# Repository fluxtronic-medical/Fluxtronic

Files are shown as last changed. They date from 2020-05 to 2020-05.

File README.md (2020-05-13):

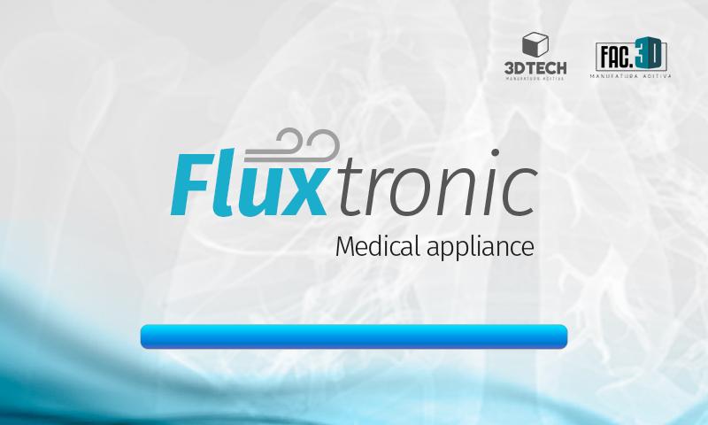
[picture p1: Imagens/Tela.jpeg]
 
 
# FLUXTRONIC
 
## ⚠️  ATENÇÃO! ANTES DE COMPARTILHAR OU REALIZAR DOWNLOADS, ESTEJA CIENTE DOS SEGUINTES ITENS:
 
**Este projeto ainda está em desenvolvimento. Não é um produto pronto e ainda não está apto a fabricação em escala. Ainda temos muito trabalho a ser feito, verifique o status do projeto e veja como pode colaborar.**
 
 **[IN PROGRESS]****[IN PROGRESS]****[IN PROGRESS]****[IN PROGRESS]****[IN PROGRESS]**
-----------------------------------------------------------------------------------------------------------------

#### Video de funcionamento do equipamento

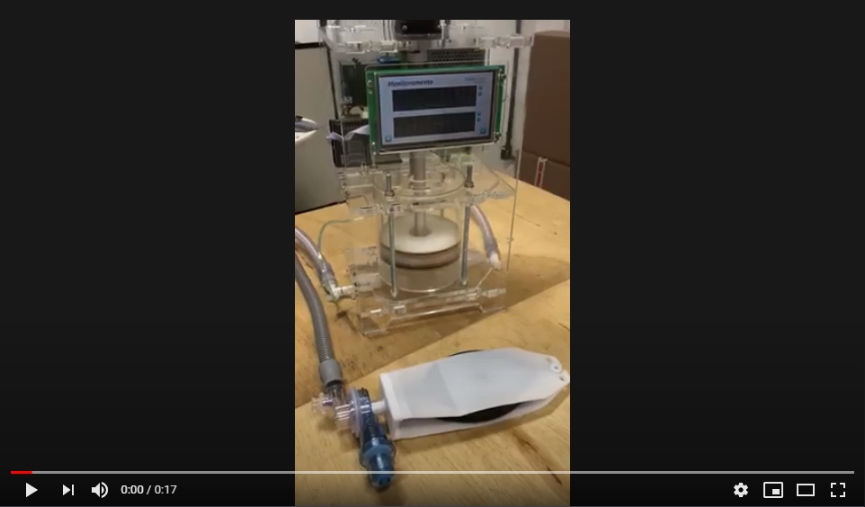
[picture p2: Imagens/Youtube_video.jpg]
Watch the video (https://www.youtube.com/watch?v=dyl--hyxr6U&feature=youtu.be)


## Porque mais um projeto?
 
Criamos outra vertente de projeto, diferente dos que já estão em desenvolvimento, pensando principalmente nas matérias primas e itens disponíveis para fabricação dentro do Brasil que são de fácil acesso. Acreditamos que esse conceito **depois de validado** possa ser replicado com o menor tempo de fabricação e com menor custo comparado a outros projetos. 

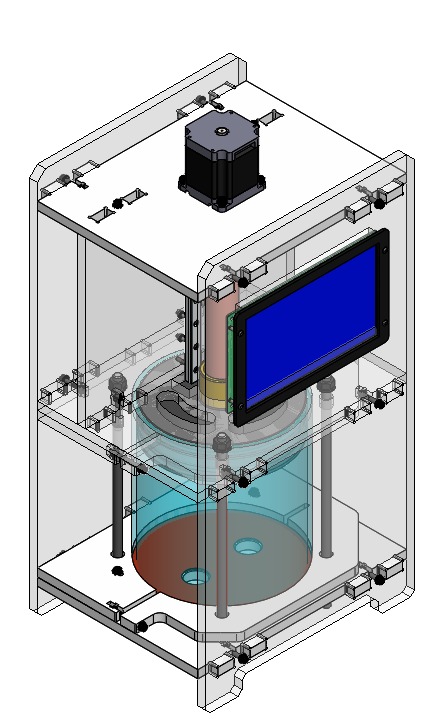
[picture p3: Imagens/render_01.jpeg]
  
# Status
 
- March 20-24: Testes mecânicos 
- March 24: Adaptação para NEMA 23 e ajustes para maior rigidez da estrutura.
- March 25: Testes de fluxo com NEMA 23 e programação do CLP.
- March 26: Programação do sistema de telemetria e controle de informações na IHM.
- March 27: Teste intenso do sistema e fadiga do equipamento
- March 28: Instalação do sensor MPX 2010 e teste de pressão
- March 29: Programação do sistema de falhas por pressão e IHM display 128x64
- March 30: Junção dos programas e limpeza do código + ~~Aferição de fluxo e pressão com equipamento de calibração~~
- March 31: Testes de alarme junto ao sistema de sensoriamento
- April 01: Liagação das válvulas e controle via CLP
- April 02: Adicionar módulo analógico CLP e comunicar via arduino
- April 03: Configuração dos equipamentos de medição para aferir o sistema + Programação CLP entrada analógica
- April 04: Migração do firmware para plataforma ESP32 | Teste e análise de fluxo
- April 05: Implementação NEXTION para leitura do gráfico + ~~ESP32~~
- April 06: Merge código de telemetria + IHM + CLP | Upload de fotos da montagem/dispositivos
- April 07: Configuração da interface IHM
- April 08: Resolução de Bug's no firmware do arduino
- April 09: Ligação do equipamento de medição (Fluxo+pressão)
- April 10: Debug IHM/arduino (comunicação serial)
- April 11: Debug IHM/arduino (comunicação serial) + adaptação válvula Peep
- April 12: Testes de sensoriamento e alarme + Mapeamento das variáveis
- April 13: Calibração da curva de respiração 
- April 14: Vídeo explicativo do sistema + avaliação Dr. Glauco Westphal

**ALTERAÇÃO DO SISTEMA MECÂNICO E ABANDONO DO ACIONAMENTO DE AMBU**

- April 15: 
- April 16:
- April 17:
- April 18:
- April 19:
- April 20:
- April 21:
- April 22:
- April 23:
- April 24:
- April 25:
- April 26:
- April 27:
- April 28:
- April 29:

### 👉 Em progresso:
 
- [x] Iniciar testes de controle de ciclo via potenciômetro
- [x] Alteração de design para junção da fixação de guia
- [x] Validação do motor NEMA 23
- [x] Validar utilização de fuso de avanço rápido 6,35x25,4 (diâmetro x passo)
- [x] Escolha do driver de motor de passo com foco em baixo custo e fácil acesso (Dimensionado p/ NEMA23)
- [x] Programação arduino para controle de ciclo e fluxo via potenciômetro
- [x] Criação da interface (espaço para 2 potenciômetros e possível tela para sensor de fluxo)
- [x] Levantamento de sensorização do sistema (qual sensor utilizar?)
- [x] Realizar testes intensivos para identificar pontos críticos nas partes de acrílico
- [x] Teste com válvulas solenóides para parada de emergência do sistema
- [x] Criação da case eletrônica
- [x] Programação CLP para leitura analógica
- [ ] ~~Controle PID do motor via CLP~~
- [x] Adaptação controle de telemetria
- [x] Testes com sensor de pressão industrial
- [ ] ~~Adaptação do código para utilização do ESP32~~
- [x] Testar MPX5010  (*06 April - Validado*)
- [x] Desenhar ligação eletrônica (Fritzing)
- [x] Armazenar os valores nas variaveis quando retornar as configurações
- [x] Corrigir bug, que faz imprimir a tela 4 antes da tela 5 quando entra em alarme de pressão pulmonar
- [x] Imprimir o valor máximo quando rotaciona o encoder no sentido anti-horário na posição mínima
- [x] Implementar saída analogica para controle de velocidade de avanço
- [x] Implementar saída analogica para controle de velocidade de recuo
- [x] Controle da curva de respiração 
- [x] Instalar nova mecânica (Atuador enclausurado)
- [x] Reunir materiais de estudo em pasta compartilhada
- [x] ~~Desligar as válvulas de inspiração/expiração e ligar a válvula de backup quando estiver em pressão pulmonar alta~~
- [ ] Desenvolvimento do Buffer de mistura 
- [x] ~~Teste do sistema blender (2-100-6016 | Oxigel)~~

### 👉 Pendente:

- [ ] Criação, validação e fabricação de PCB para entrada dos sensores e saída do motor
- [ ] Levantamento de fornecedores e estoques no Brasil dos itens de projeto
- [ ] Plotar gráfico de volume IHM
- [ ] Calibração geral dos sensores (intervalos mínimos e máximos)
- [ ] Implementação do sensor de fluxo 
- [ ] Validação das válvulas de controle I/E
- [ ] Sensor de oxigênio (Célula de oxigênio)
- [ ] Mapeamento do sistema de filtragem
- [ ] Fluxograma de controle
- [ ] Desenvolvimento do manual de operação
- [ ] Desenvolvimento material gráfico vista explodida + apresentação
- [ ] Diagrama de funcionamento do sistema
- [ ] Teste do sensor de fluxo - [ Ventilator Inline Sensor Package ](https://hackaday.io/project/170622-visp-ventilator-inline-sensor-package)

# Requisitos principais
 
1. Be reliable. It must work continuously without failure (100% duty cycle) for blocks of 14days — 24 hours a day. If necessary, the machine may be replaced after each block of 14 days x 24 hours a day use.
 
2. Provide at least two settings for volume of air/air O2 mix delivered per cycle/breath. These settings to be 450ml +/- 10ml per breath and 350ml +/- 10ml per breath.
 
3. Provide this air/air O2 mix at a peak pressure of 350 mm H2O.
 
4. Have the capability for patient supply pipework to remain pressurised at all times to 150mm H20.
 
5. Have an adjustable rate of between 12 and 20 cycles/breaths per minute.
 
6. Deliver at least 400ml of air/air 02 mix in no more than 1.5 seconds. The ability to change the rate at which air is pushed into the patient is desirable but not essential.

## Lista de material (BOM) [IN PROGRESS]

### Mecânica: 
 
- 1x Fuso DST-LS-10X25-R-ES (160mm)
- 1X Castanha DST-JFRM-C-01-DS10X25
- 1x Acoplamento para motor de passo
- 1x Patins Mgn12
- 1x Trilho Mgn12 (180mm)

#### Corte a laser (acrílico)

|       CÓDIGO         | QUANTIDADE | Espessura |
|----------------------|------------|-----------|
|   8003.200.00.01     |     01     |   10mm    |
|   8003.200.00.02     |     01     |   10mm    |
|  8003.200.00.02-1    |     01     |   10mm    |
|   8003.200.00.03     |     01     |   10mm    |
|   8003.200.00.04     |     01     |   10mm    |
|   8003.200.00.05     |     01     |   10mm    |
|   8003.200.00.06     |     01     |   10mm    |
|   8003.200.00.07     |     01     |   10mm    |
|   8003.300.00.01     |     01     |   03mm    |

### Eletrônica: 
 
- 1x Nema 23 15kg

- 1x Arduino uno
- 1x Driver de motor de passo **(DM322E)**
- 1x CLP Panasonic FP0R-C16T
- 2X Módulos de entrada/saída (8 canais)
- 1x Módulo analógico CLP (AFP0RA42)
- ~~2x Potênciometro 1K~~
- ~~1x Display 128x64~~
- 1x Encoder KY040
- 1x Fonte 24V 5A
- 1x Sensor de pressão MPX5010dp
- 1x Sensor de fluxo HAFUHH0050L4AXT
- 1x Tela Nextion 7pol
- 1x Sensor fim de curso mecânica
- 1x Fita LED (RGB)

 ### Itens médicos:

 - 1x Adaptador para conexão válvula PEEP
 - 3x tubo traqueia
 - 1x Válvula para ambu PEEP (5-20cmH20)
 - 2x Conector "Y" 22mx15F
 - 3x Fluxômetro para oxigênio
 - 1x Filtro HMEF
 - 1x Filtro HEPA

#  Material para estudo
 
Não deixe de ler sobre o assunto e entender melhor sobre como funciona um ventilador, quais suas principais funções em relação a ventilação de pacientes com COVID-19 e também alguns editais sobre:
 
- [Rapidly manufactured ventilator system specification](https://www.gov.uk/government/publications/coronavirus-covid-19-ventilator-supply-specification/rapidly-manufactured-ventilator-system-specification)
- [Specification for ventilators to be used in UK hospitals during the coronavirus (COVID-19) outbreak](https://www.gov.uk/government/publications/specification-for-ventilators-to-be-used-in-uk-hospitals-during-the-coronavirus-covid-19-outbreak)
- [Frontier Tech 4 COVID Action: emerging market ventilation systems](https://medium.com/frontier-technology-livestreaming/frontier-tech-4-covid-action-emerging-market-ventilation-systems-9c818cb46189)
- [Positive Ending Expiratory Pressure Valve](https://grabcad.com/library/positive-ending-expiratory-pressure-valve-1)
- [ANVISA By Flavia G. R. Ibagy Pacheco](https://drive.google.com/open?id=1CEK9-QgvEUpADV46hfBZcp89tQX-wVuy)

# Créditos

* Helbert Paranhos [@HPparanhos](github.com/HPparanhos) - SC
* Fellipy Kuhne  [@kinife](https://github.com/kinife) - SC
* José Manuel Ramirez [@tere.red](http://tere.red/) - SC
* Rodrigo França Formaggi [@Rodrigoformagi](https://www.linkedin.com/in/rodrigo-fran%C3%A7a-formaggi-88b730103/) - SC
* Erick Henriques Paulo Boteon [@Erick Boteon](https://www.linkedin.com/in/erick-boteon-5601a416b/) - SC
---------------------------------------------------------------------------------------------------------------
 
   > É preciso alinhar a expectativa de todos! Estamos trabalhando duro no processo de validação e rápida modificação para um projeto 100% confiável e esperamos ao máximo que isso possa salvar muitas vidas!

# ✅ Licença

Este projeto detém uma licença para produção, fabricação e desenvolvimento. Para que não hajam problemas no decorrer do tempo, é imprescindível que as mesmas sejam respeitadas e seguidas. Para mais informações acesse: 
[GNU General Public License v3.0](https://github.com/fluxtronic-medical/Fluxtronic/blob/master/LICENSE)

*Tire todas suas dúvidas antes de replicar e/ou desenvolver este projeto*

# 💰 Apoiar financeiramente

Para avançar com rapidez precisamos da sua ajuda! Saiba como colaborar com o projeto em - [DOAR](https://www.vakinha.com.br/vaquinha/acelerar-o-desenvolvimento-do-respirador-mecanico-opensource)

# Contatos e redes sociais

* Telegram [Grupo de desenvolvimento](https://t.me/joinchat/PWSd9VVRa-Q0fzXPvgVH4g)
* Instagram [@fluxtronic](https://www.instagram.com/fluxtronic/)
* Twitter [Fluxtronic - Respirador Open Source](https://twitter.com/FluxtronicOpen)
* Site Oficial [Fluxtronic.com.br](https://fluxtronic.com.br/)
* Imprensa [Fale conosco](https://web.whatsapp.com/send?phone=5547996113022)

# Empresas que apoiam essa causa

- AMS Group
- 3D Acrilicos
- Pollux Automation
- Neoyama
- Bold acrílicos
- Unimed Joinville
- OBR Equipamentos industriais
- Igus do Brasil
- JN Ferramentaria
- Docol
- Valgri
- Nidec (Embraco)
- TEX Equipamentos Eletrônicos
- Termica Solutions
- Tere.Red
- Ocotea Filmes
- Microjunta
- SR Borrachas
- Andre Toledo

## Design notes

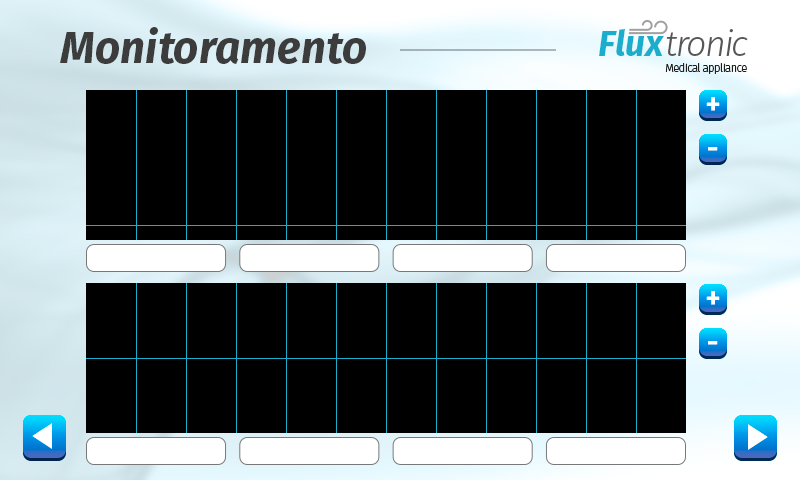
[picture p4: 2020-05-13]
IHM/Telas.png/Graficos.png

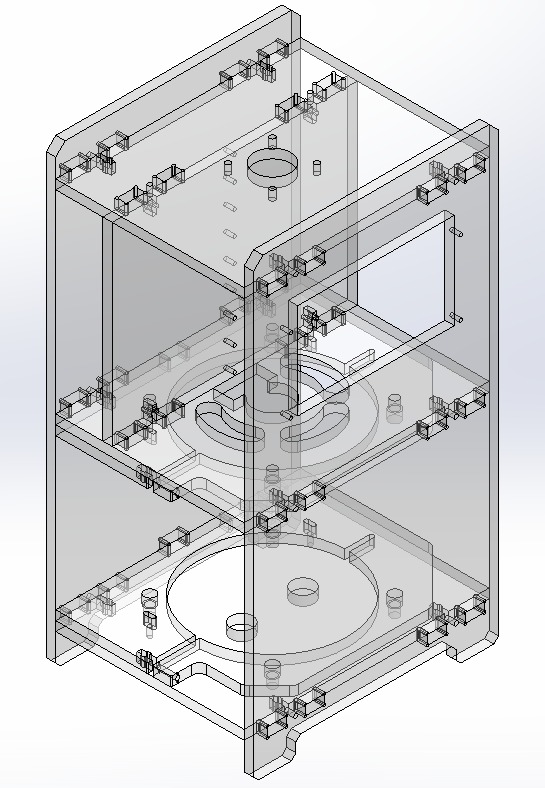
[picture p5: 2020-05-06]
Imagens/render_02.jpeg

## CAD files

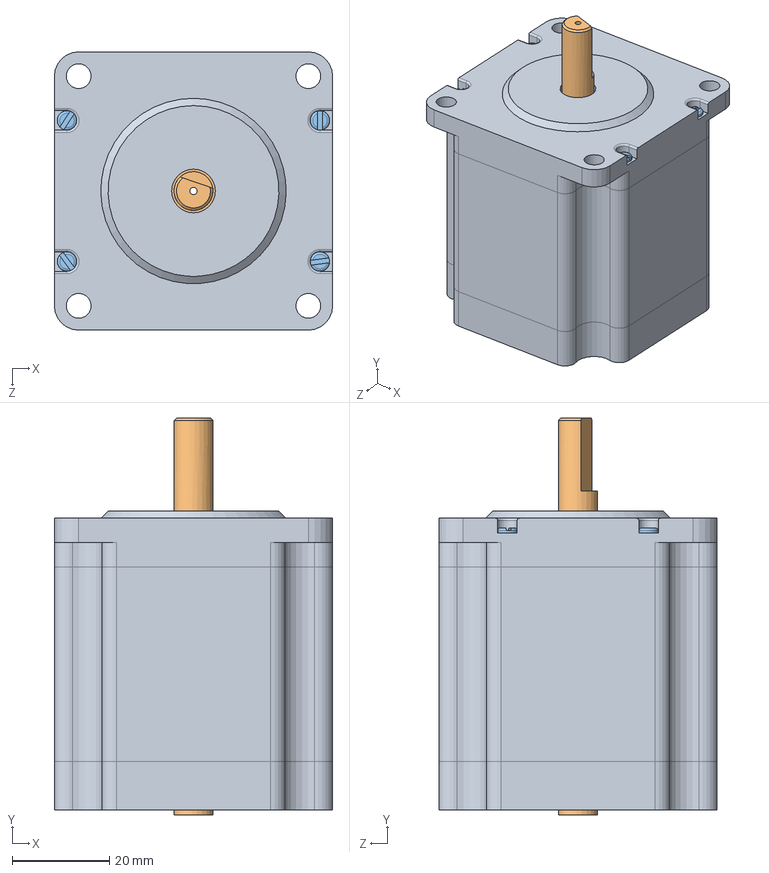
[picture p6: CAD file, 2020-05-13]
3D Model/NEMA23.SLDASM
57.2 x 81.6 x 57.2 mm
NEMA23
inside
Pin x 4

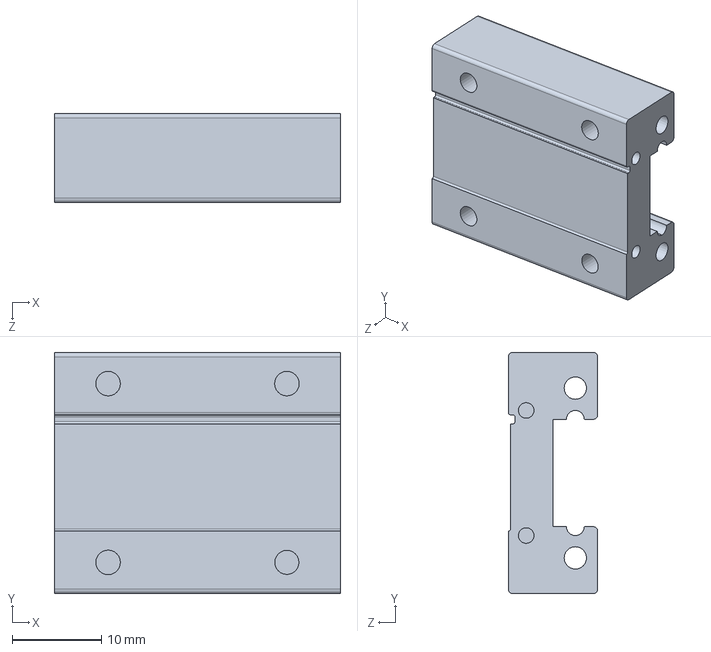
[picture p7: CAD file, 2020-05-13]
3D Model/Main Block.SLDPRT
32.0 x 27.0 x 10.0 mm

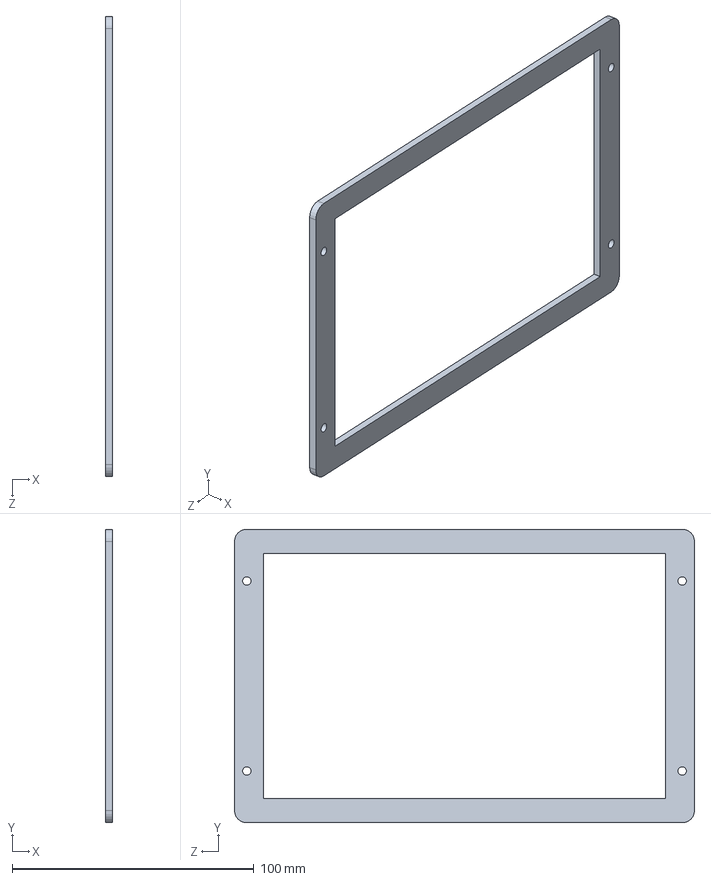
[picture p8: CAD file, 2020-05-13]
3D Model/8003.300.00.00.SLDASM
3.00 x 121.4 x 190.3 mm

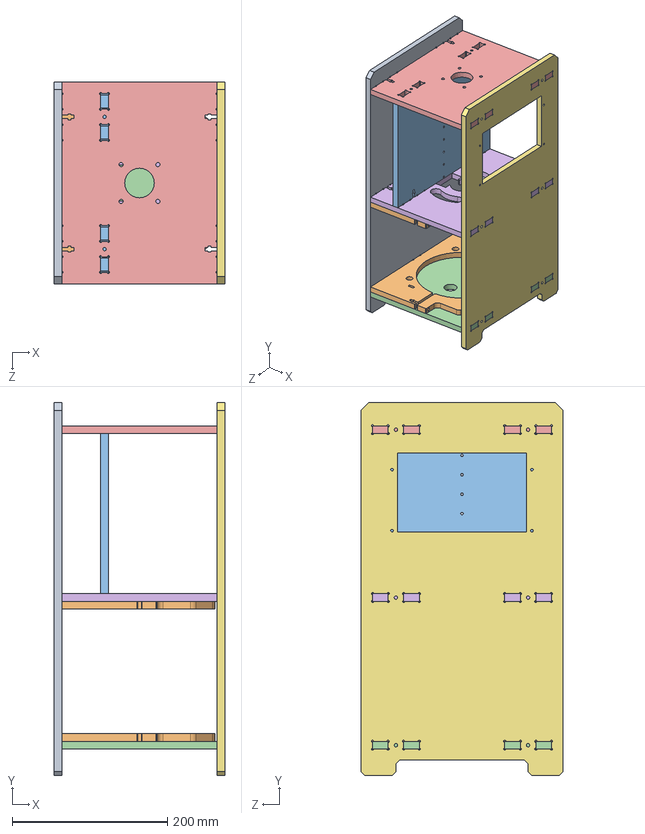
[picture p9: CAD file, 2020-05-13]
3D Model/8003.200.00.00.SLDASM
220.0 x 480.0 x 260.0 mm

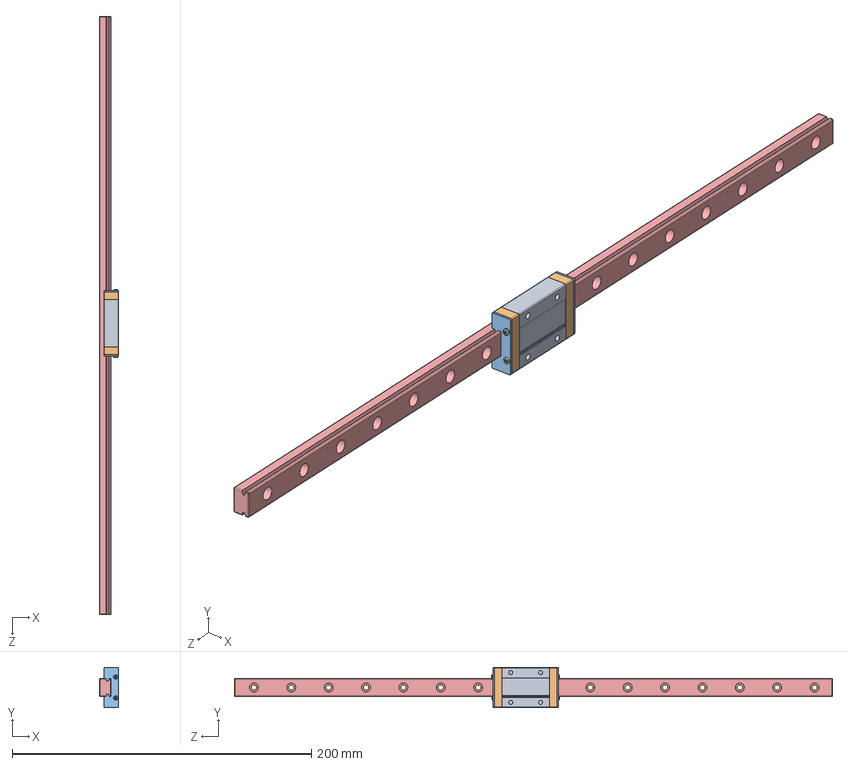
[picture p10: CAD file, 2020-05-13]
3D Model/8003.100.10.00.SLDASM
13.0 x 27.0 x 400.0 mm
Main Block
Green End Cap x 2
Red End Cap x 2
Button M3x8 x 4
Rail 400mm

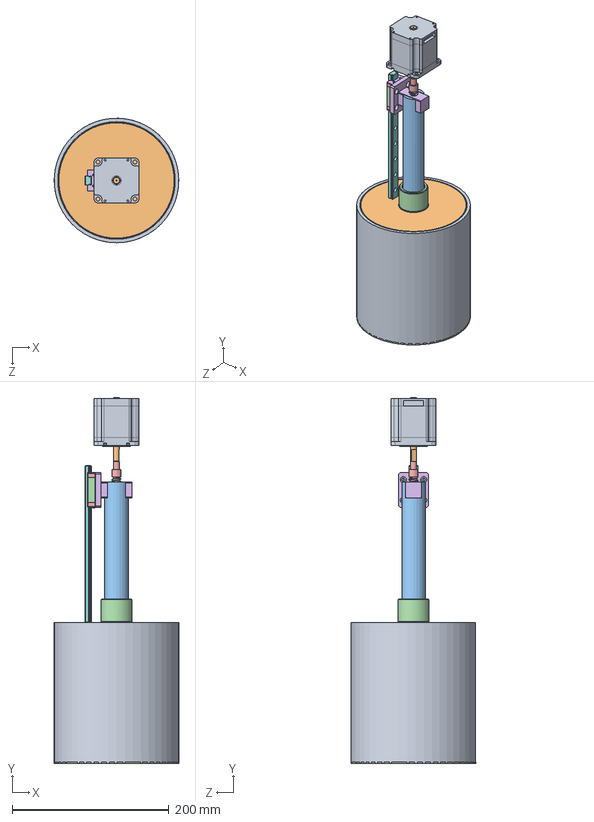
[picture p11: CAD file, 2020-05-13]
3D Model/8003.100.00.00.SLDASM
159.0 x 467.0 x 159.0 mm
Main Block
Green End Cap x 2
Red End Cap x 2
Button M3x8 x 4
Rail 400mm
NEMA23
inside
Pin x 4
Винт Z
Tr12x3 Block

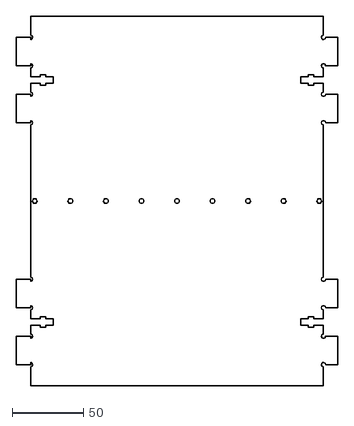
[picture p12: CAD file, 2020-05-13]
2D Model/8003.200.00.03.DXF
226.0 x 260.0

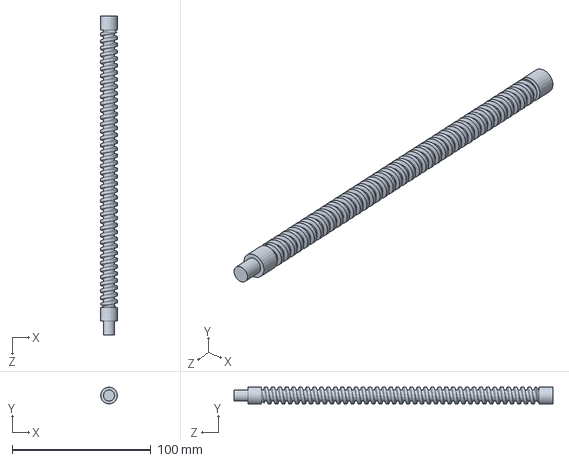
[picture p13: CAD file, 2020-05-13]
3D Model/Винт Z.SLDPRT
12.0 x 12.0 x 230.0 mm

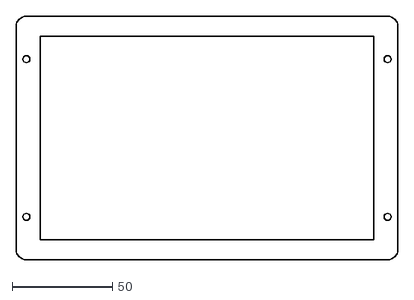
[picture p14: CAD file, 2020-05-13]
2D Model/8003.300.00.01.DXF
190.3 x 121.4

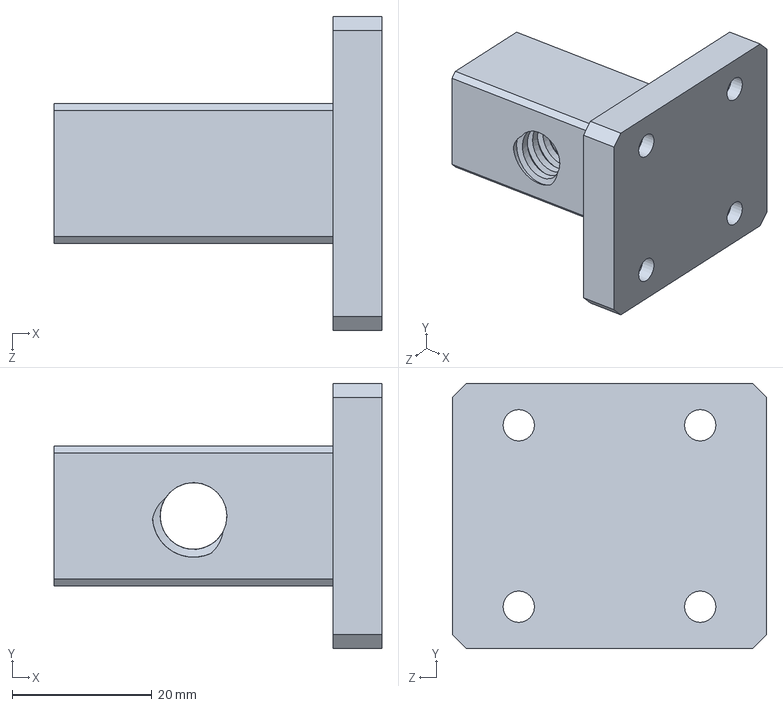
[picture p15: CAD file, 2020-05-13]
3D Model/Tr12x3 Block.SLDPRT
47.0 x 38.0 x 45.0 mm

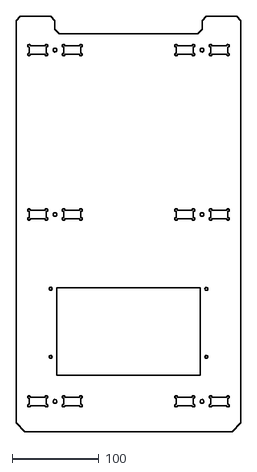
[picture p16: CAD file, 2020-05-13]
2D Model/8003.200.00.07.DXF
260.0 x 480.0

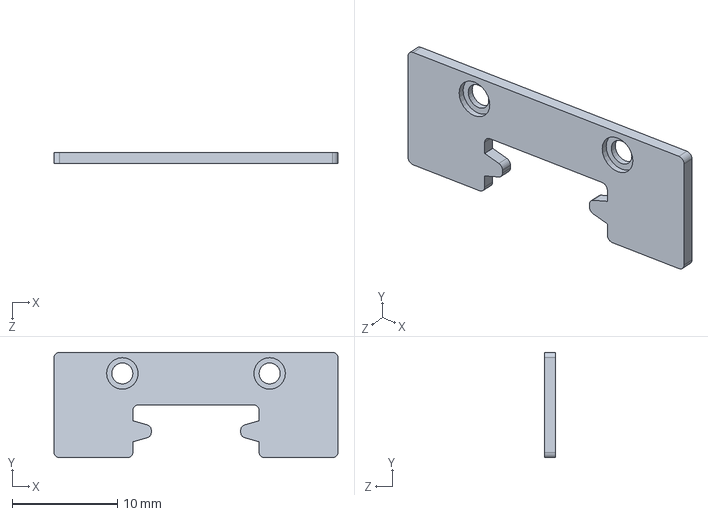
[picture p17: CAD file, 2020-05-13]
3D Model/Red End Cap.SLDPRT
27.0 x 10.0 x 1.00 mm

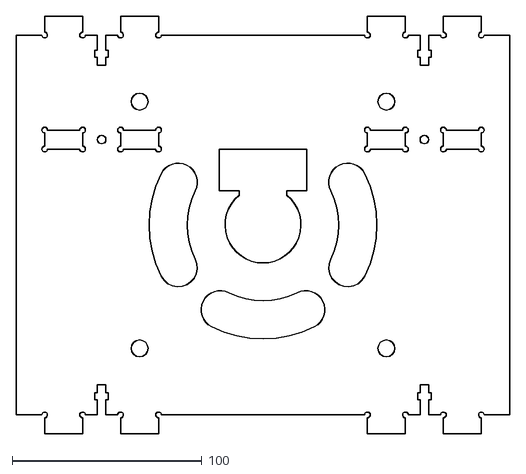
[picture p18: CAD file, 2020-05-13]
2D Model/8003.200.00.06.DXF
260.0 x 220.0

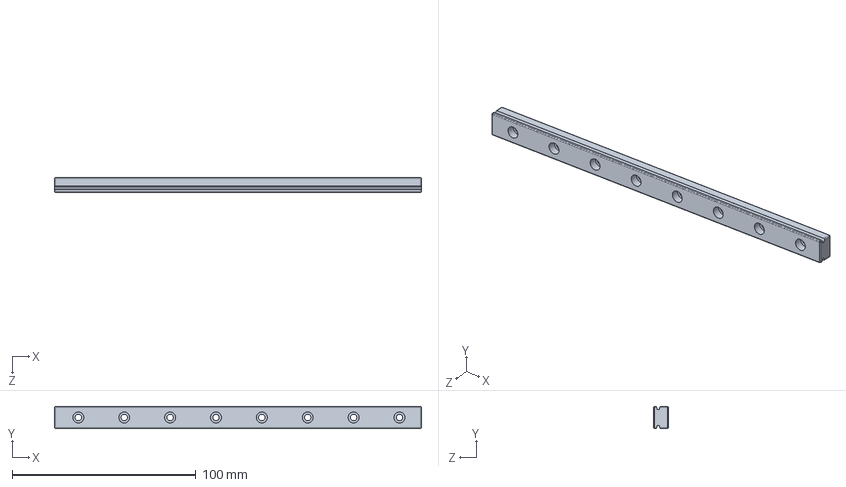
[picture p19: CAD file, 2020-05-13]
3D Model/Rail 400mm.SLDPRT
200.0 x 12.0 x 8.00 mm

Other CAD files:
2D Model/8003.200.00.05.DXF
3D Model/Pin.SLDPRT
2D Model/8003.200.00.04.DXF
3D Model/Peça1.SLDPRT
2D Model/8003.200.00.01.DXF
2D Model/8003.200.00.02-1.DXF
2D Model/8003.200.00.02.DXF
3D Model/39019.010.00.00.03.SLDDRW
3D Model/39019.010.00.00.03.SLDPRT
3D Model/39019.010.00.00.04.SLDDRW
3D Model/39019.010.00.00.04.SLDPRT
3D Model/8003.100.00.01.SLDPRT
3D Model/8003.100.00.02.SLDPRT
3D Model/8003.100.00.03.SLDPRT
3D Model/8003.100.00.04.SLDPRT
3D Model/8003.100.00.05.SLDPRT
3D Model/8003.200.00.01.SLDPRT
3D Model/8003.200.00.02.SLDPRT
3D Model/8003.200.00.03.SLDPRT
3D Model/8003.200.00.04.SLDPRT
3D Model/8003.200.00.05.SLDPRT
3D Model/8003.200.00.06.SLDPRT
3D Model/8003.200.00.07.SLDPRT
3D Model/8003.300.00.01.SLDPRT
3D Model/BARRA M8 X 250.SLDPRT
3D Model/Button M3x8.SLDPRT
3D Model/Green End Cap.SLDPRT
3D Model/NEMA23.SLDPRT
3D Model/P80480V70C_T30.SLDPRT
3D Model/P80480V70C_T30.stp
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

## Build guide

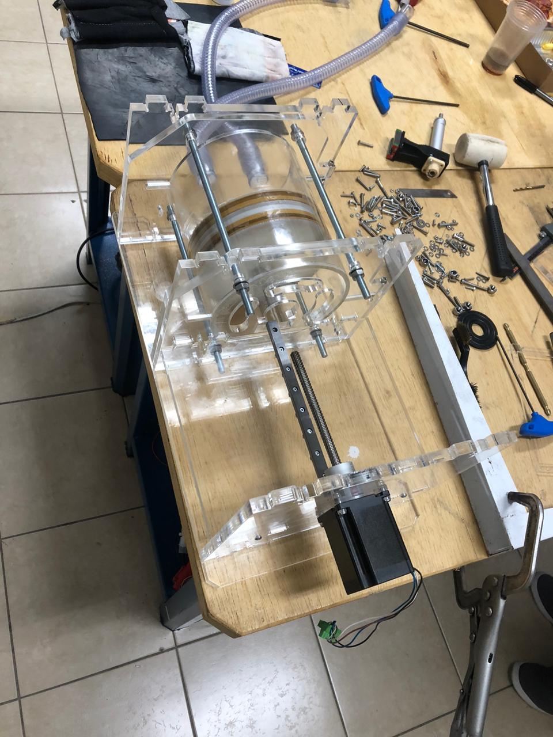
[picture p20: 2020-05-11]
Manual de montagem/Fotos montagem/03.jpeg

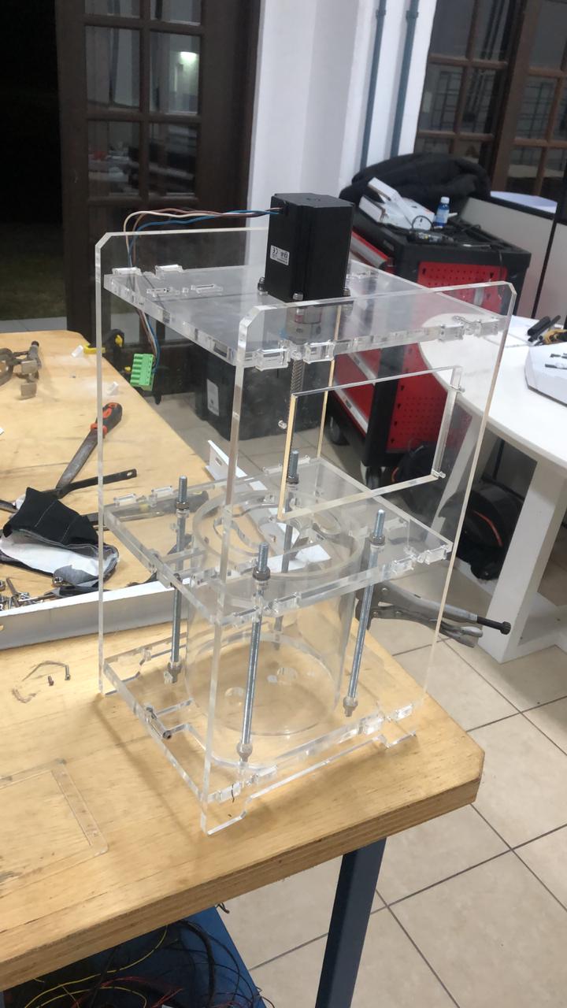
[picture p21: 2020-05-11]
Manual de montagem/Fotos montagem/05.jpeg

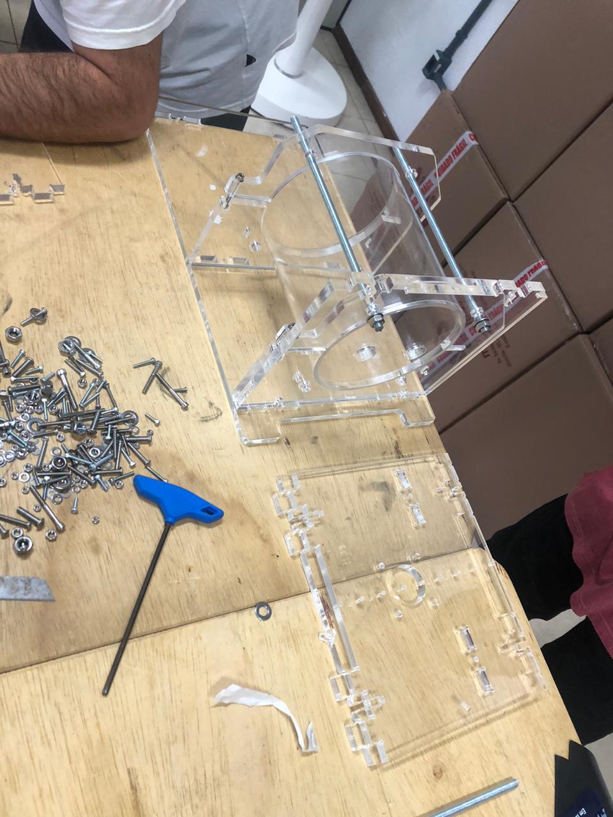
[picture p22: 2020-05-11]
Manual de montagem/Fotos montagem/06.jpeg

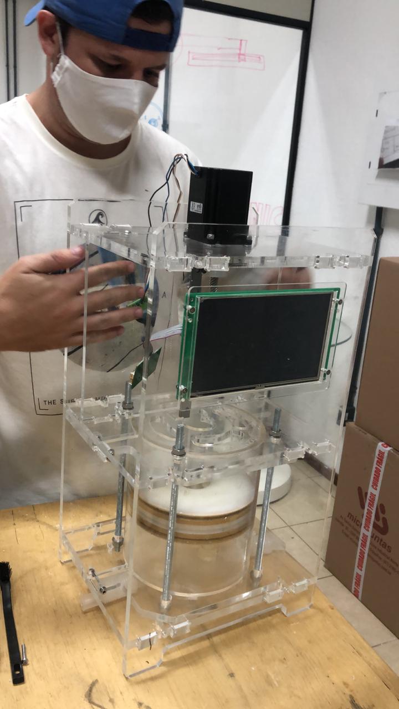
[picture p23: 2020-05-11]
Manual de montagem/Fotos montagem/01.jpeg

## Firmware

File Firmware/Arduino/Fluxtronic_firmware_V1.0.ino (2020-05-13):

#include <Adafruit_MCP4725.h>
#include <UnicViewAD.h>
#include <Wire.h>


LCM Lcm(Serial);
Adafruit_MCP4725 dacToProg;

#define     num    10         //número de iterações da média móvel
#define     rangePmax 1020    //Pressão maxima que o sensor mpx5010 consegue medir (mmH2O)
#define     rangePmin 0       //Pressão minima que o sensor mpx5010 consegue medir (mmH2O)
#define     maxPressure 1000.l  //Range máximo de pressão

#define REDPIN 9
#define GREENPIN 10
#define BLUEPIN 11 

long moving_average(int sig);
int values[num];              //vetor com num posições, armazena os valores para cálculo da média móvel


int ins_valve = 2;         // rele que aciona valvula de inspiração
int ex_valve = 4;          // rele que aciona valvula de expiração
int aO_progress = 3;       //saída analógica para clp que controla o avanço maximo do pistao
int aO_speed = 5;          //saida analogica para clp que controla a velocidade do pistão
int a1_MPX5010 = 1;        //sensor de pressao

unsigned long intervalEx = 0;
unsigned long intervalIns = 0;
unsigned long previousMillisIns = 0;
unsigned long previousMillisEx = 0;
unsigned long startMillis;
unsigned long currentMillis = 0;
unsigned long timerGraph = 20;
unsigned long previousMillisGraph = 0;
unsigned long previousMillisPage = 0;
unsigned long previousMillisAlarm = 0;
unsigned long timerPage = 5;
unsigned long lapsusIns = 0;
unsigned long lapsusEx = 0;

LcmVar t_ins(0);
LcmVar freq_res(6);
LcmVar volume(12);
LcmVar debug1(30);
LcmVar debug2(36);
LcmVar debug3(18);
LcmVar t_ex(24);
LcmVar i(42);
LcmVar e(48);
LcmVar refresh_button(100);
LcmVar pressure(54);
LcmVar p_max(60);
LcmVar p_min(70);

const int pic_intro1 = 0;
const int pic_intro2 = 1;
const int pic_intro3 = 2;
const int pic_intro4 = 3;
const int pic_intro5 = 4;
const int pic_intro6 = 5;
const int pic_intro7 = 6;
const int pic_setup = 7;
const int pic_monitor = 9;
const int refresh_value = 1000;
int pic_Id = 0;


int val_p_max = rangePmin;
int val_p_min = rangePmax;
int val_t_ins = 0;
int val_t_ex = 0;
int val_freq_res = 0;
int val_volume = 0;
int val_debug1 = 0;
int val_debug2 = 0;
int val_debug3 = 0;
const int val_i = 1;
int val_e = 0;
//---------------
int last_t_ins = 0;
int last_t_ex = 0;
int last_freq_res = 0;
int last_volume = 0;
int updateSum = 0;
//---------------
int analog_volume=0;
int analog_pressure = 0;

void setup() {
  Lcm.begin(115200);
  dacToProg.begin(0x60);
  pinMode(aO_progress, OUTPUT);
  pinMode(aO_speed, OUTPUT);
  pinMode(ins_valve, OUTPUT);
  pinMode(ex_valve, OUTPUT);
  pinMode(REDPIN, OUTPUT);
  pinMode(GREENPIN, OUTPUT);
  pinMode(BLUEPIN, OUTPUT);

  digitalWrite(ins_valve, LOW);
  digitalWrite(ex_valve, LOW);
  byte version = 0xFF;
  while (version == 0xFF)
  {
    version = Lcm.readFirmwareVersion();
  }
  
  
  Lcm.changePicId(pic_intro1);
  delay(500);
  Lcm.changePicId(pic_intro2);
  delay(700);
  Lcm.changePicId(pic_intro3);
  delay(300);
  Lcm.changePicId(pic_intro4);
  delay(500);
  Lcm.changePicId(pic_intro5);
  delay(1000);
  Lcm.changePicId(pic_intro6);
  delay(1500);
  Lcm.changePicId(pic_intro7);
  delay(500);
  Lcm.changePicId(pic_setup);
  startMillis = millis();
}

int arduinoToDisplay(float f , int fator) {
  int inteiro = 0;
  inteiro = f * fator;
  return inteiro;
}

float displayToArduino(int inteiro, int divisor) {
  float f;
  f = inteiro / divisor;
  return f;
}

void loop() {
  currentMillis = millis();
  pic_Id = Lcm.readPicId();
  lapsusIns = currentMillis - previousMillisIns;
  lapsusEx = currentMillis - previousMillisEx;

  if (pic_Id == 7) {
    updateSetup();
    analogWrite(REDPIN, 0);
    analogWrite(GREENPIN, 0);
    analogWrite(BLUEPIN, 255);

  }
  if (pic_Id == 9) {
    updatePressure();
  }
  val_volume     = volume.read();
  analog_volume = map(val_volume,0,1000,0,4095);
  dacToProg.setVoltage(analog_volume, false);
}


// ========================================================================================================
// --- Desenvolvimento das Funções ---
long moving_average(int sig)
{
  int i;               //variável auxiliar para iterações
  long acc = 0;        //acumulador
  //Desloca o vetor completamente eliminando o valor mais antigo
  for (i = num - 1; i > 0; i--) values[i] = values[i - 1];
  values[0] = sig;           //carrega o sinal no primeiro elemento do vetor
  for (i = 0; i < num; i++) acc += values[i];
  return acc / num;         //Retorna a média móvel
}


void updatePressure() {
  int grafico = 0;             //armazena a leitura filtrada da entrada analógica
  int adc_noise1 = 0;             //armazena a leitura sem filtro da entrada analógica

  if (currentMillis - previousMillisGraph >=  timerGraph) {
    analogWrite(REDPIN, 0);
    analogWrite(GREENPIN, 255);
    analogWrite(BLUEPIN, 0);
    adc_noise1 = analogRead(a1_MPX5010);
    grafico = map( moving_average(adc_noise1), 0 , 1023, 0, 1020);

    Lcm.writeTrendCurve0(grafico);
    previousMillisGraph = currentMillis;
    pressure.write(grafico);

    if (grafico > val_p_max) {
      val_p_max = grafico;
      p_max.write(val_p_max);
    }//if

    if (grafico < val_p_min) {
      val_p_min = grafico;
      p_min.write(val_p_min);
    }//if
    if (grafico >= (maxPressure)) {
      Lcm.beepBuzzer(255);
      analogWrite(REDPIN, 255);
      analogWrite(GREENPIN, 0);
      analogWrite(BLUEPIN, 0);
      Lcm.activateSoftwareControl(200);
    }//if

  }//if
}//updatePressure

void updateSetup() {
  val_t_ins     = t_ins.read();
  val_t_ex      = t_ex.read();
  val_freq_res  = freq_res.read();
  //val_e         = e.read();
  //if (t_ins.read() != 0 && freq_res.read() != 0) {
  //val_t_ex = ((6000 - (val_t_ins * val_freq_res)) / val_freq_res);
  // calcValTempEx();
  //t_ex.write(val_t_ex);
  //val_e = val_t_ex / val_t_ins;
  //calcValIE();
  //calcValTempInsp();
  //e.write(val_e * 100);
  // }
  updateVariables();
}

// *volume (0,1000) ml
// *tempo inspiracao (0,5) seg (dec,2)
// *tempo expiracao inspiracao (0,5) seg (dec,2)
// *pausa inspiratoria (0,1) seg (dec,2)
// *freq respiratoria (0,30) int
// rel ins vs ex 1 : (tExp / tInsp)
/*
  [t-ins] [f-res] [t-exp] [I:E]
  [vol]
*/

void calcValFreqResp() {
  int dividor = val_t_ins + val_t_ex;
  if (dividor > 0 && val_t_ins > 0 && val_t_ex > 0) {
    val_freq_res = 6000 / dividor;
    freq_res.write(val_freq_res);
  }
}
void calcValTempEx() {
  if (val_t_ins > 0 && val_freq_res > 0) {
    val_t_ex = ((6000 - (val_t_ins * val_freq_res)) / val_freq_res);
    if (val_t_ex == 0) {
      calcValFreqResp();
    }
    else {
      t_ex.write(val_t_ex);
    }
  }
}

void calcValTempInsp() {
  if (val_t_ex > 0 && val_freq_res > 0) {
    val_t_ins = ((6000 - (val_t_ex * val_freq_res)) / val_freq_res);
    t_ins.write(val_t_ins);
  }
}
void calcValIE() {
  if (val_t_ins > 0) {
    val_e = val_t_ex / val_t_ins;
    e.write(val_e * 100);
  }
}

void updateVariables() {
  // val_e
  // last_volume = 0;
  //if(last_t_ins > 0 && last_t_ex > 0 && last_freq_res > 0){
  if (val_t_ins != last_t_ins) { //-- calc [f-res] [t-exp] [I:E]
    updateSum++;
    if (updateSum > 1) {
      calcValTempEx();
      calcValFreqResp();
      calcValIE();
    }
  }
  if (val_t_ex != last_t_ex) { //-- calc [t-ins] [f-res] [I:E]
    updateSum++;
    if (updateSum > 1) {
      calcValFreqResp();
      calcValTempInsp();
      calcValIE();
    }
  }
  if (val_freq_res != last_freq_res) { //-- calc [t-ins] [t-exp] [I:E]
    updateSum++;
    if (updateSum > 1) {
      calcValTempInsp();
      calcValTempEx();
      calcValIE();
    }
  }
  // }//if
  last_t_ins = val_t_ins;
  last_t_ex = val_t_ex;
  last_freq_res = val_freq_res;
}//

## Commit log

2020-05-13 Create BARRA M8 X 250.SLDPRT
    [BARRA M8 X 250.SLDPRT]
2020-05-13 Create Button M3x8.SLDPRT
    [Button M3x8.SLDPRT]
2020-05-13 Create Green End Cap.SLDPRT
    [Green End Cap.SLDPRT]
2020-05-13 Create Main Block.SLDPRT
    [Main Block.SLDPRT]
2020-05-13 Create Rail 400mm.SLDPRT
    [Rail 400mm.SLDPRT]
2020-05-13 Create Red End Cap.SLDPRT
    [Red End Cap.SLDPRT]
2020-05-13 Create Tr12x3 Block.SLDPRT
    [Tr12x3 Block.SLDPRT]
2020-05-13 Create Винт Z.SLDPRT
    [Винт Z.SLDPRT]
2020-05-13 Create Fluxtronic_firmware_V1.0.ino
    Atualização de pastas e arquivos arduino
